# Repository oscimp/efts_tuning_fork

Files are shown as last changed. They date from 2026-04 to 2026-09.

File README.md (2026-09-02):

# <a href="https://efts.eu">European Frequency and Time Seminar (EFTS)</a> quartz tuning fork laboratory session.

A quartz tuning fork packaged in a transparent casing is used to demonstrate
* closed loop oscillation using a Negative Impedance Converter (NIC) circuit (<a href="oscillator/oscillateur_1night.png">Allan deviation</a> below $10^{-9}$ up to 30 s integration time).
* openloop stroboscopic imaging of the quartz prong motion driven by sound card output.

<a href=kicad/>KiCAD</a> board design files.



## References:

### Hardware (using a <a href="stroboscopy/IMG_20260409_120540_544.jpg">Raspberry Pi5</a> single board computer for running GNU Radio for controlling the sound card and recording the video stream):
* 32768 Hz tuning fork in transparent package: <a href="https://eu.mouser.com/ProductDetail/Epson-Timing/FC-135-32.7680KA-AC5?qs=f9yNj16SXrLM6nHs1T34rQ%3D%3D">Epson FC-135 32.7680KA-AC5</a> (0.404 euros/p)
* sound card with sampling rate 96 kHz or higher, e.g. <a href="https://www.amazon.fr/-/en/UGREEN-External-Headphones-Compatible-Raspberry/dp/B08Y8CZB2S/">UGREEN (10.2 euros on amazon)</a> although a <a href="http://www.thomann.fr/focusrite_scarlett_solo_3rd_gen.htm">Focusrite Scarlett Solo</a>
(89 euros but 192 kS/s at 24 bits) might be a wiser choice if can be afforded (see <a href="stroboscopy/">bottom of this page</a>).
* "digital microscope" webcam, e.g. <a href="https://amscope.co.uk/products/c-hhd510-w">AmScope HHD Series</a> (~50 euros)
* 7414 Schmitt trigger (0.5 to 0.7 euros)
* 7400 NAND gate (0.2 to 0.3 euros)

**Note**: the single board computer **must** be a RPi5 and **not** a RPi4 whose USB bus is too unstable to generate a clean audio signal probing
the narrow tuning fork resonance. See the <a href="stroboscopy">stroboscopy</a> subdirectory for the demonstration.

### Software

* use ``mplayer tv://`` to display the webcam output (or ``vlc`` if it displays properly in the
selected window manager): allows for stretching the image to full screen even if recording a "poor" 
webcam resolution (640x480) stream from the digital microscope.
* GNU Radio <a href="stroboscopy/snd.grc">flowchart</a> for driving the two channels of the
stereo sound card (tested with GNU Radio 3.10) with 1 Hz offset between the signal driving
the tuning fork and the stroboscopic signal driving the LED.
* Maybe wise to ``echo "performance" > /sys/devices/system/cpu/cpu0/cpufreq/scaling_governor`` 
to run the CPUs at maximum speed (will heat to 65 degC).

## Resources:

Equivalent BvD model of the quartz tuning fork (see <a href="KeysightE4990A/">the impedance analyzer</a> measurement):
* R1=53727 $\Omega$
* L1=7221 H
* C1=3.268 fF
* C0=3.368 pF

Quality factor $Q=\frac{1}{R1}\sqrt{\frac{L1}{C1}}=27700$

Resonance frequency $f=\frac{1}{2\pi\sqrt{L1\cdot C1}}=\frac{1}{2\pi\sqrt{7221\times 3.268\cdot 10^{-15}}}=32763$ Hz

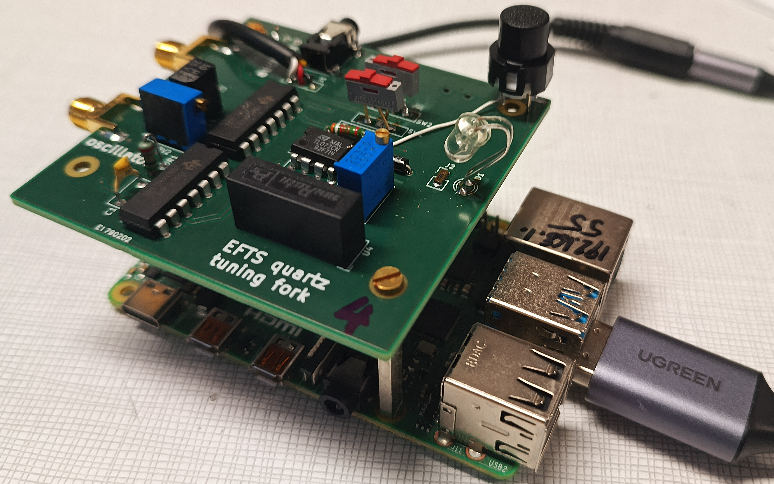
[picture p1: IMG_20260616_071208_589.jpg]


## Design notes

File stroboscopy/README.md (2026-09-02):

# Experimental setup: adjusting the LED position to illuminate the tuning fork

## Preliminary tests 

Notice that this picture is misleading as it shows a Raspberry Pi 4 which should
be avoided (see the bottom of this page) and replaced with a Raspberry Pi 5.

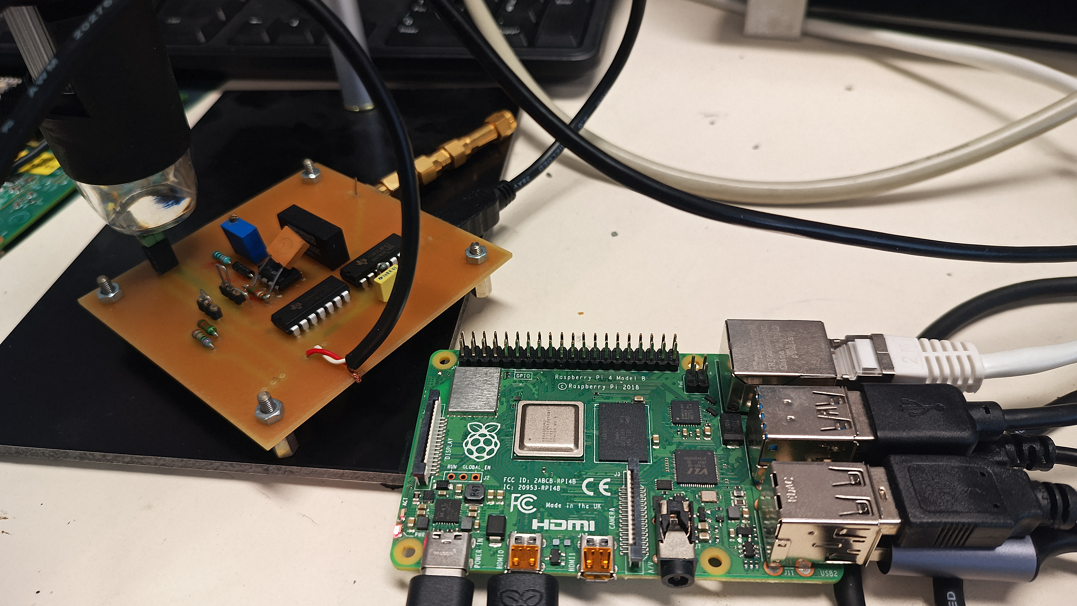
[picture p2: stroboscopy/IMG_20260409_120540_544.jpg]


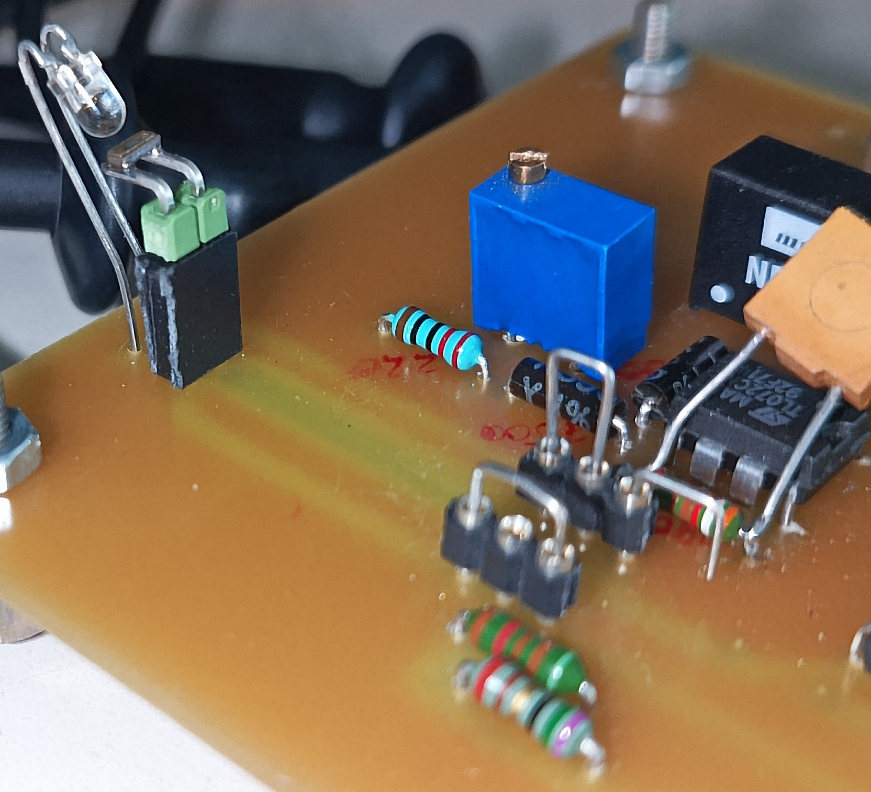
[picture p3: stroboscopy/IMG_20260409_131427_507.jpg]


## Oscilloscope screenshots: pulse driving the LED

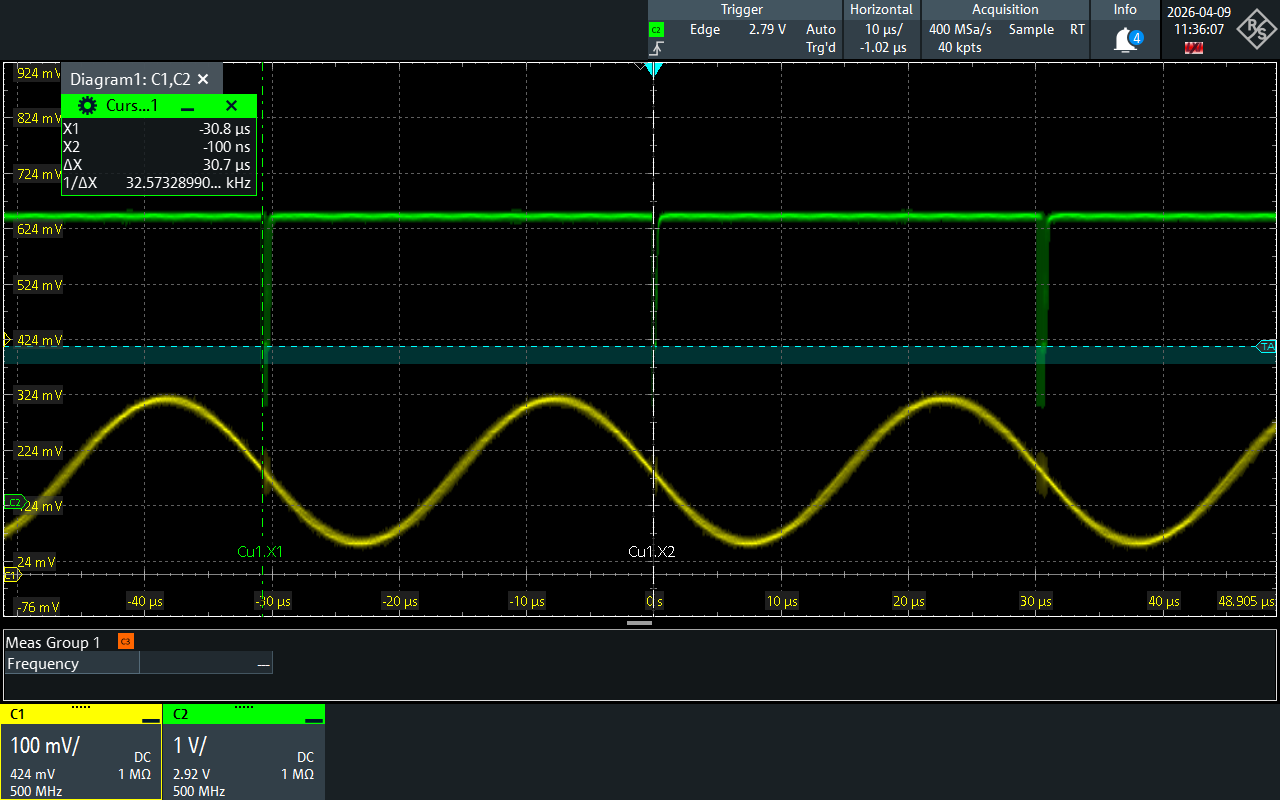
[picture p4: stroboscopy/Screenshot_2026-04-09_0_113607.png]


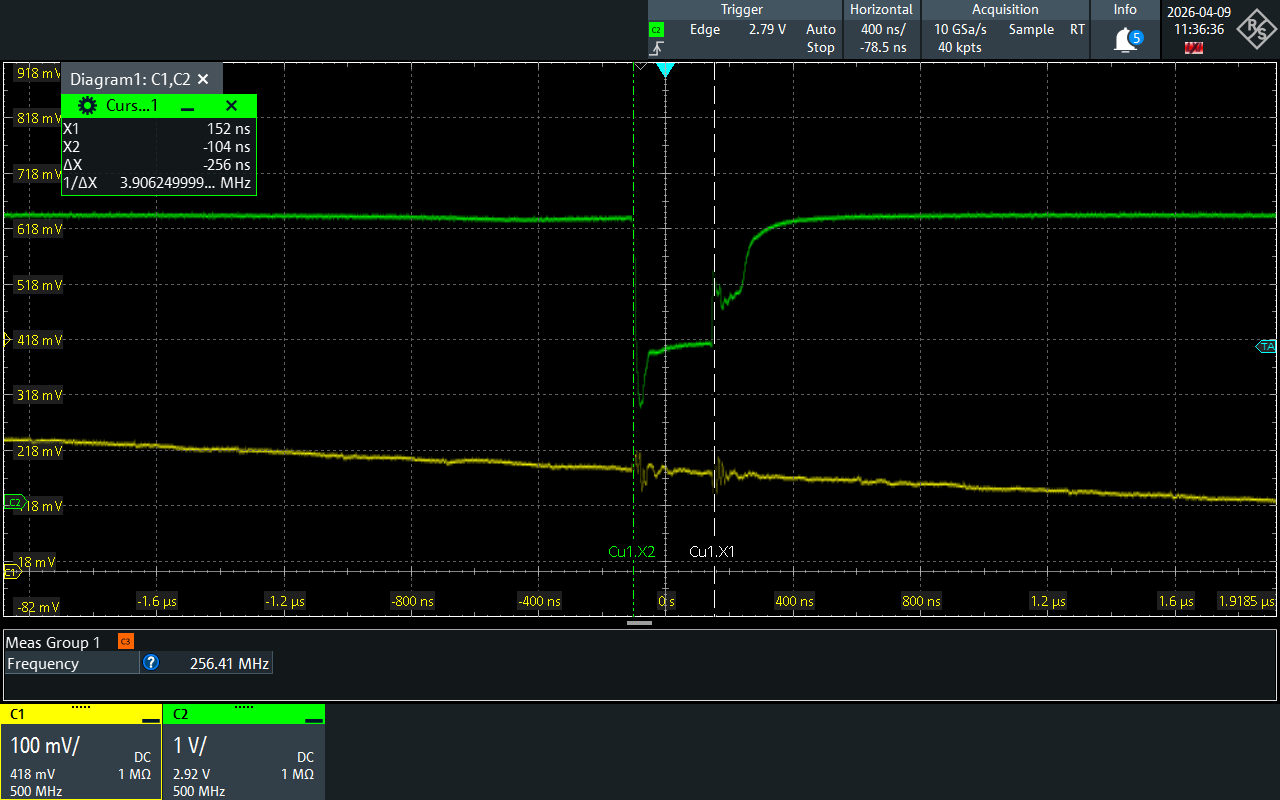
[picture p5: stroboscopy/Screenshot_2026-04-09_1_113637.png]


## Final setup

* On the Raspberry Pi: start the graphical user interface (``startx``),
open a terminal and launch ``alsamixer`` to check the sound card setting. Using F6,
select the USB sound card and check that the volume is maximum.

* Quit ``alsamixer`` and launch ``gnuradio-companion`` with the ``snd.grc`` flowgraph.
Select a frequency around 32764 Hz (a few Hz below 32768).

* Connect SPDT SW1 pin 1 to 2 (openloop measurement by driving the
tuning fork with the sound card) and SPDT SW2 1 to 3 (75 ohm load)

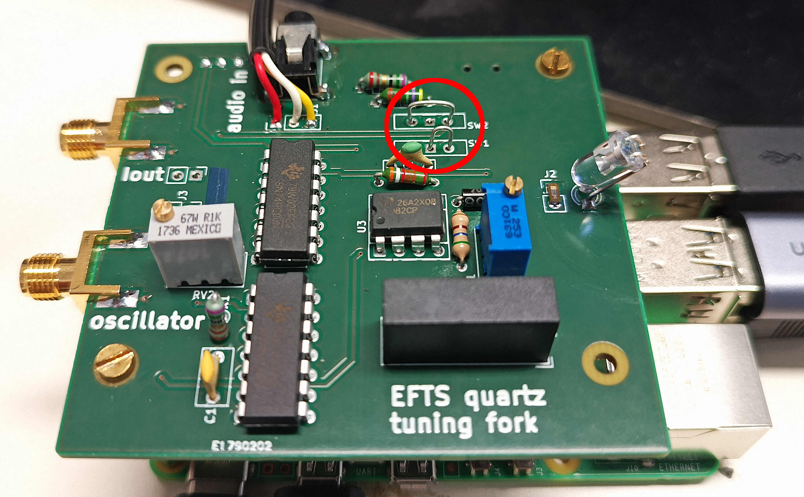
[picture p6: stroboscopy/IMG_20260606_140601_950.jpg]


* Adjust the voltage on pin 1 of the 7414 U2A using RV2

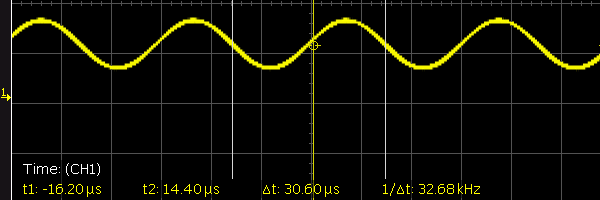
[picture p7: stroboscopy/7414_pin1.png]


so that its output in pin 2 toggles with
a more or less 50% duty cycle:

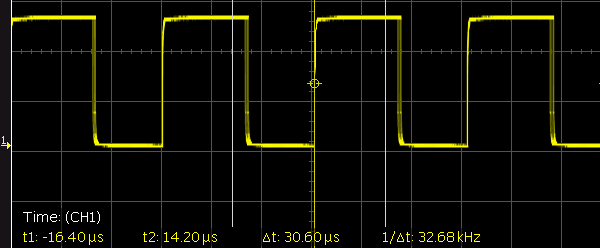
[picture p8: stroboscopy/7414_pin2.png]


* the voltage driving the LED must be a sharp negative pulse allowing the LED
to illuminate briefly the tuning fork:

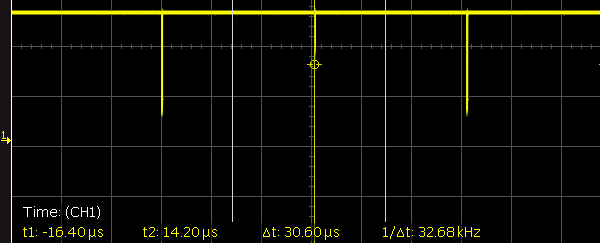
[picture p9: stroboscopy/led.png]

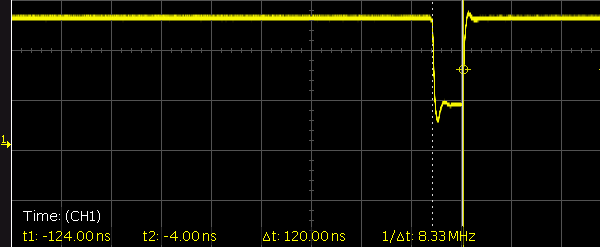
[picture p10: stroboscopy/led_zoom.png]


* check that the signal driving the tuning fork reaches the pin closest to the DC-DC
switching supply:

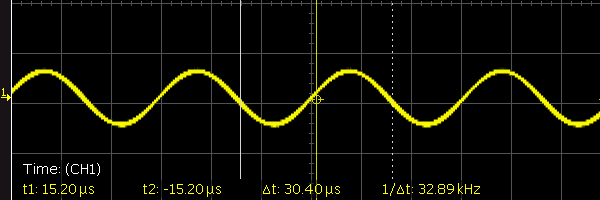
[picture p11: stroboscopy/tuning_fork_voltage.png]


* adjust the microscope position for the tuning fork picture to be centered and sharp

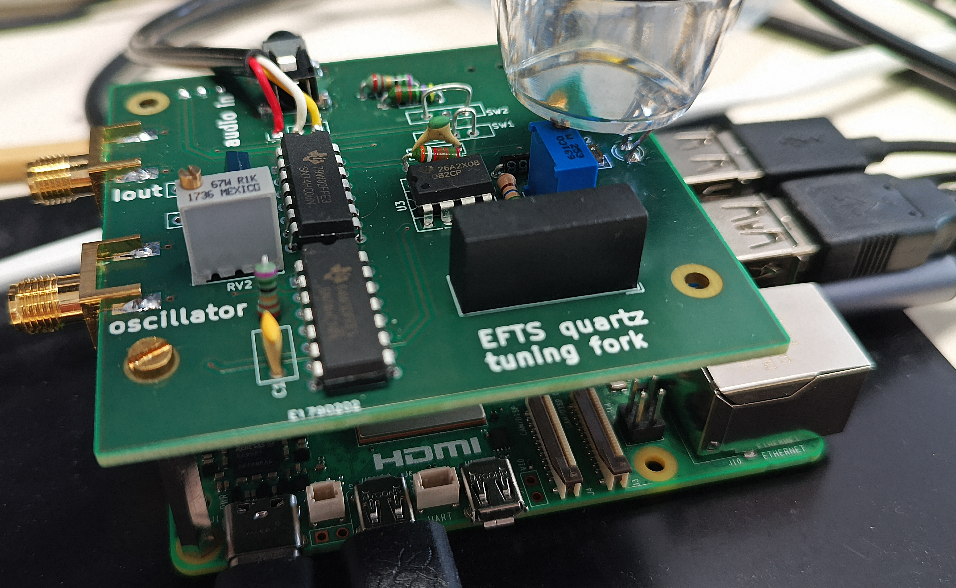
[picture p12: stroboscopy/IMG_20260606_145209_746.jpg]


<a href="https://superuser.com/questions/556029/how-do-i-convert-a-video-to-gif-using-ffmpeg-with-reasonable-quality">Converting AVI to animated GIF</a>:

```
ffmpeg -i vlc-record-2026-05-13-09h10m45s-v4l2____dev_video0-.avi -vf "fps=10,scale=320:-1:flags=lanczos,split[s0][s1];[s0]palettegen[p];[s1][p]paletteuse" -loop 0 vlc-record-2026-05-13-09h10m45s-v4l2____dev_video0-.gif
```

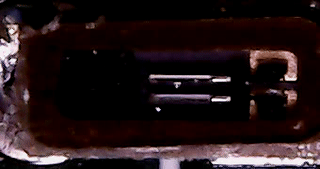
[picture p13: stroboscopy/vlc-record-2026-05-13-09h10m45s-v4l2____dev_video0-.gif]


## Automated mechanical displacement amplitude measurement

The script ``analyze.py`` replaces ``mplayer`` or ``vlc`` for collecting and displaying
images, but additionnally analyzes the displacement by correlating a reference measurement
in the first frame with all subsequent frames at the same location, marked with a green
line on each frame. The position and orientation of the green line is hardcoded, so the
tuning fork should be moved until one of the prongs is intersected by the green line. The
position is displayed in the terminal along the amplitude identified as the standard deviation
of a ring buffer collecting the position measurements. The pixel position is also saved in
``/tmp/pixel`` for plotting (e.g. GNU Octave as shown below) allows for recovering the sine-shaped
motion of the prong

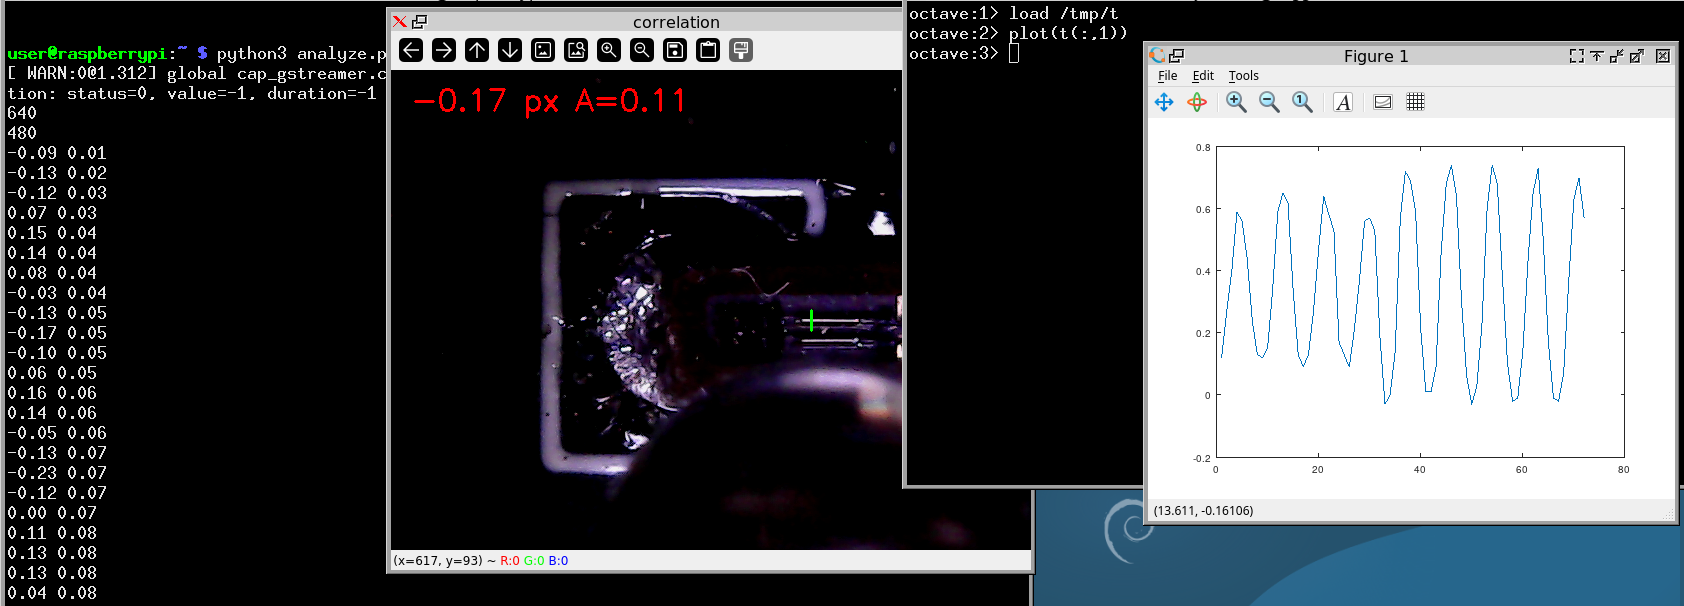
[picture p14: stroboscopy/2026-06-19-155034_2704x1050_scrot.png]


or using the GNUPlot script ``displ.plt`` which refreshes every second with the last 40
samples (vibration amplitude analysis window).

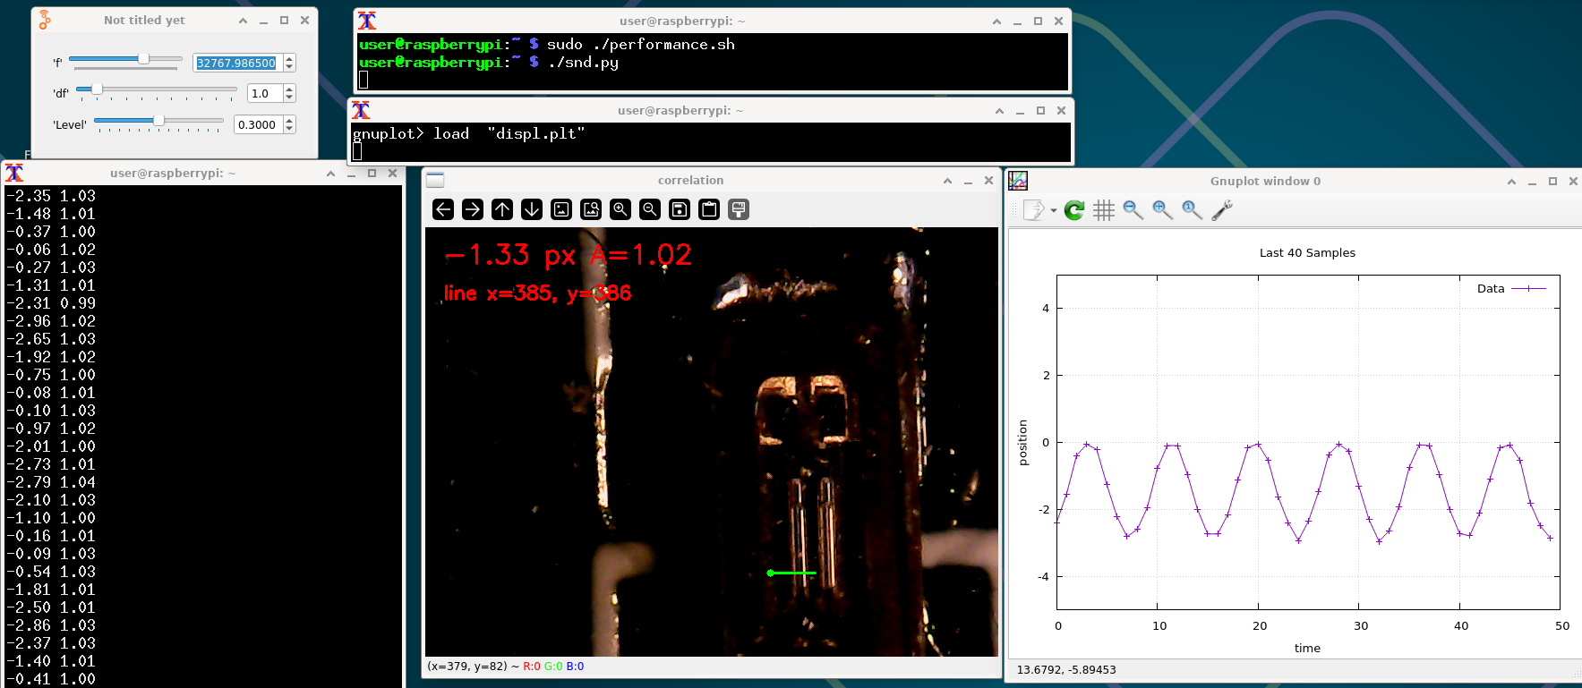
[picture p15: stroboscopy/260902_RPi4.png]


Executing ``analyze.py`` assumes that the package ``python3-opencv`` is installed.

## Problem with the RPi4 USB interface

Running a constant tone at the tuning fork resonance frequency on a Raspberry Pi 4 and
monitoring the current through the 50 kohm resistor between the tuning fork and ground exhibits
some unexpected jumps attributed to unstable signal generation by the sound card:

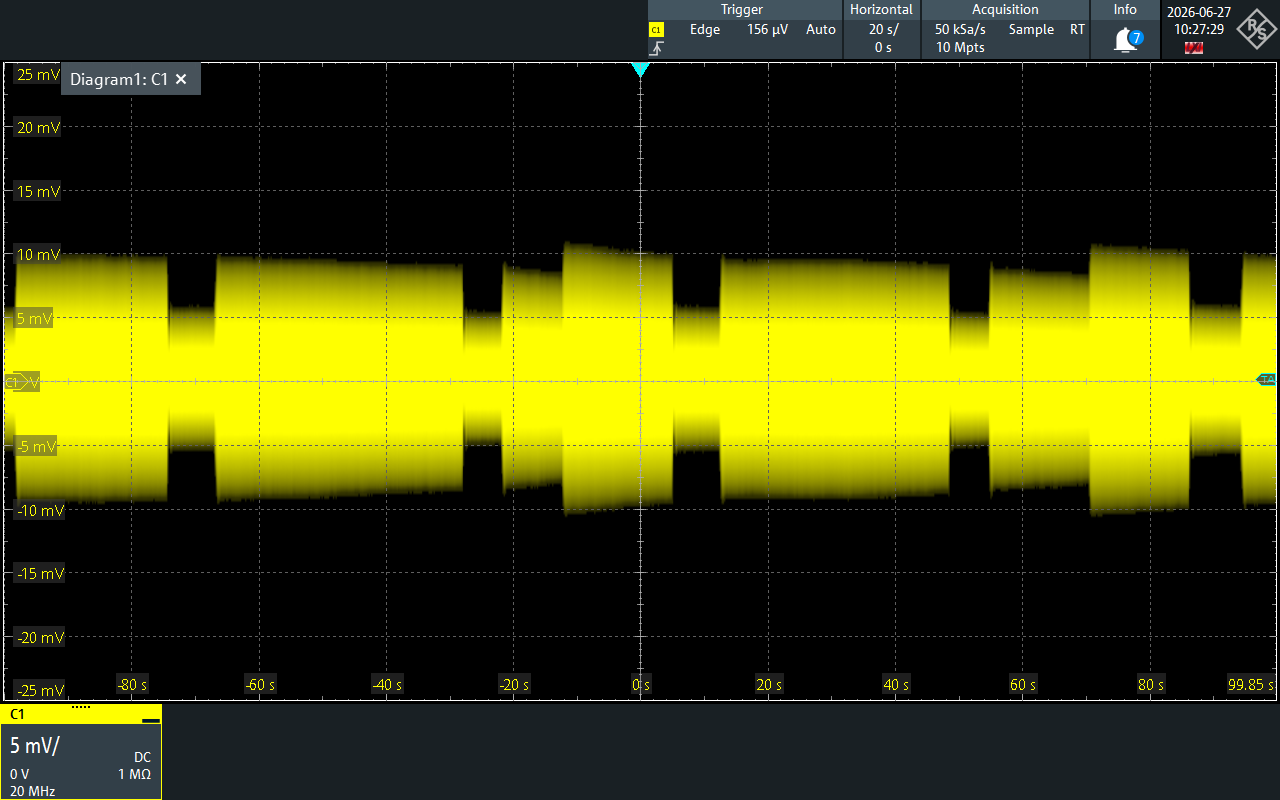
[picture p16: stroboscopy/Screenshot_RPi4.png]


most probably attributed to the poor latency performance of the RPi4 USB.

Same experiment on the Raspberry Pi 5, except at the end (80 s abscissa) when the frequency
was shifted by -2 Hz and back +2Hz on purpose to check that indeed the sound card was probing the 
tuning fork.

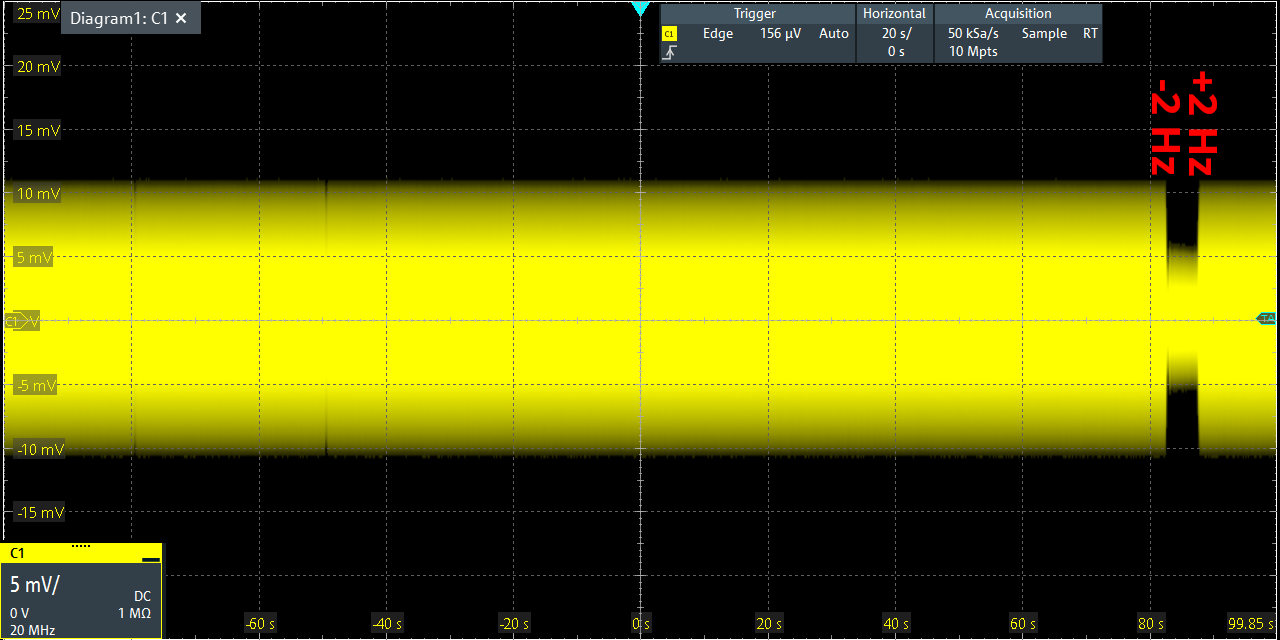
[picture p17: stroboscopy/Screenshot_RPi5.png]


Update Sept. 2026: long term measurements on the RPi5 also show some glitches on the sound card output

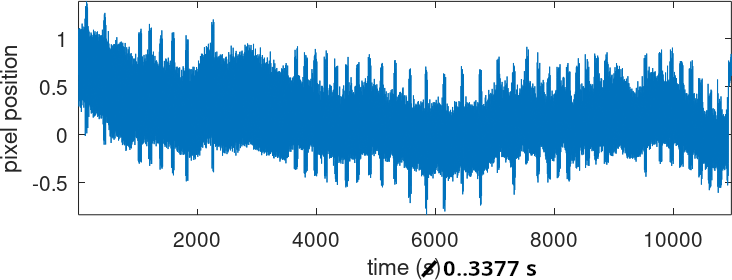
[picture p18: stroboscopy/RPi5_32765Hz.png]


although less pronounced than on the RPi4 under the same conditions.

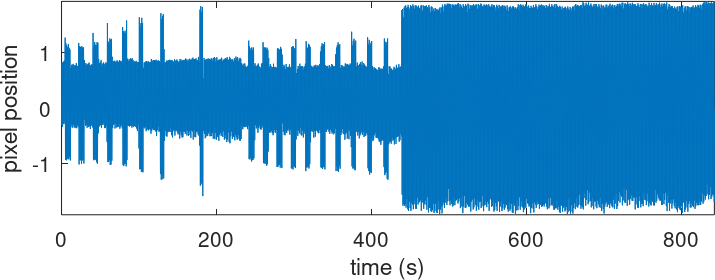
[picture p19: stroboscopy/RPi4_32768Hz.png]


A Scarlett Focusrite 18i8 provides much improved stability (and additional bandwidth and 24-bit quantization, at 10x the cost):

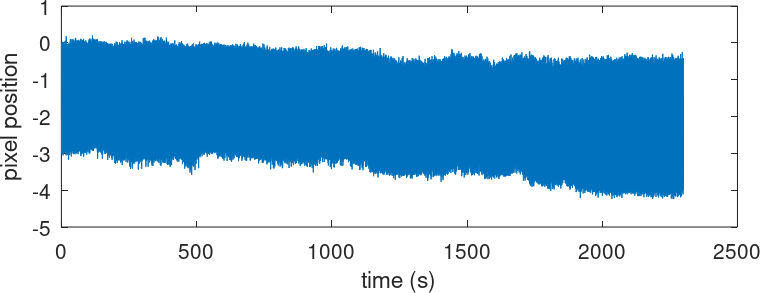
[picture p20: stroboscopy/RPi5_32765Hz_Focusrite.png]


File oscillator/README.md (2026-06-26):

See http://jmfriedt.free.fr/08520429.pdf for the description of the negative impedance circuit (Fig.3, page 7 of the PDF)
even though here any operational amplifier (e.g. TL72, TL82) will allow the 32768 Hz oscillator to start.

# Closed loop oscillator circuit

The startup time can be as long as a few minutes (hundreds of seconds).

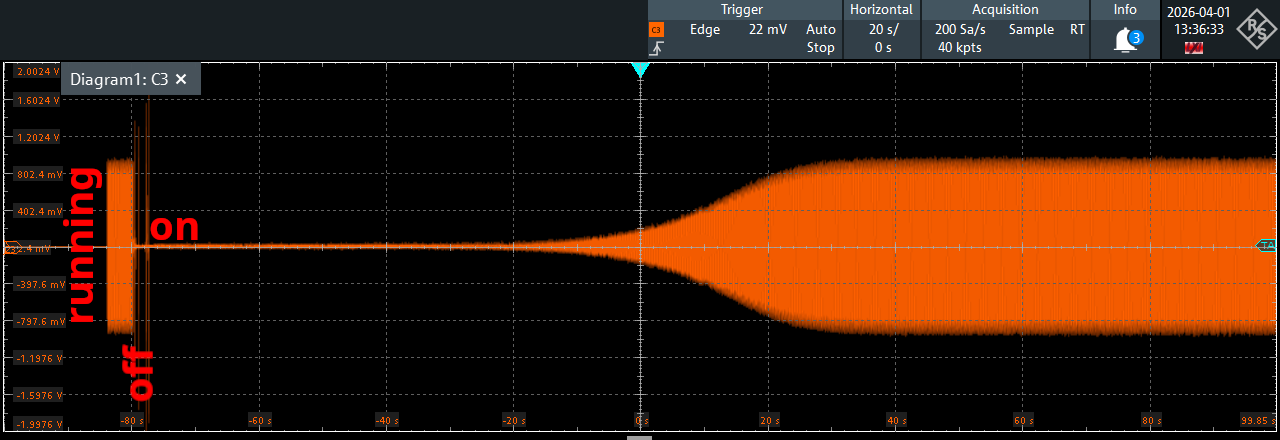
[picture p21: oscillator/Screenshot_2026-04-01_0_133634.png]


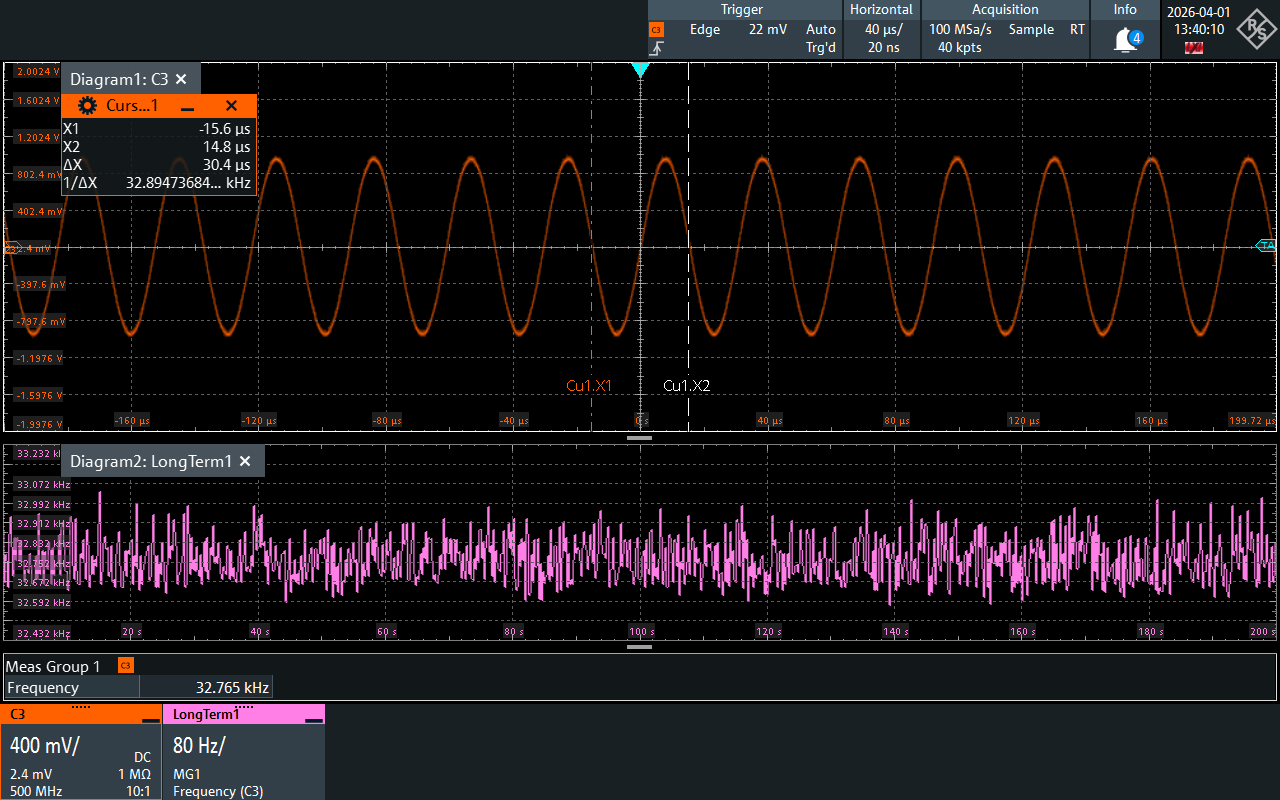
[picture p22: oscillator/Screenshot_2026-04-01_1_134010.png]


The modified Allan deviation of the frequency recording over one night
exhibits a sub- $10^{-9}$ relative frequency instability up to 30 second
integration time.

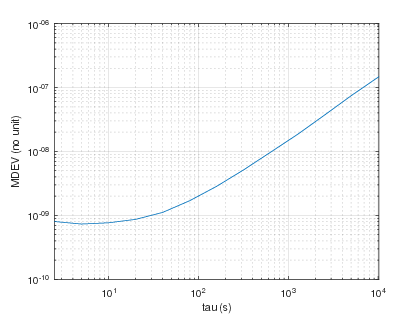
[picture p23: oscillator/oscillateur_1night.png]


## Setup

C4 was fitted with a 1 nF capacitor. In case the oscillator fails to start even at
the highest potentiometer value, remove C4.

* Close SW1 pin 2 and 3 to connect the tuning fork to the negative impedance converter circuit.

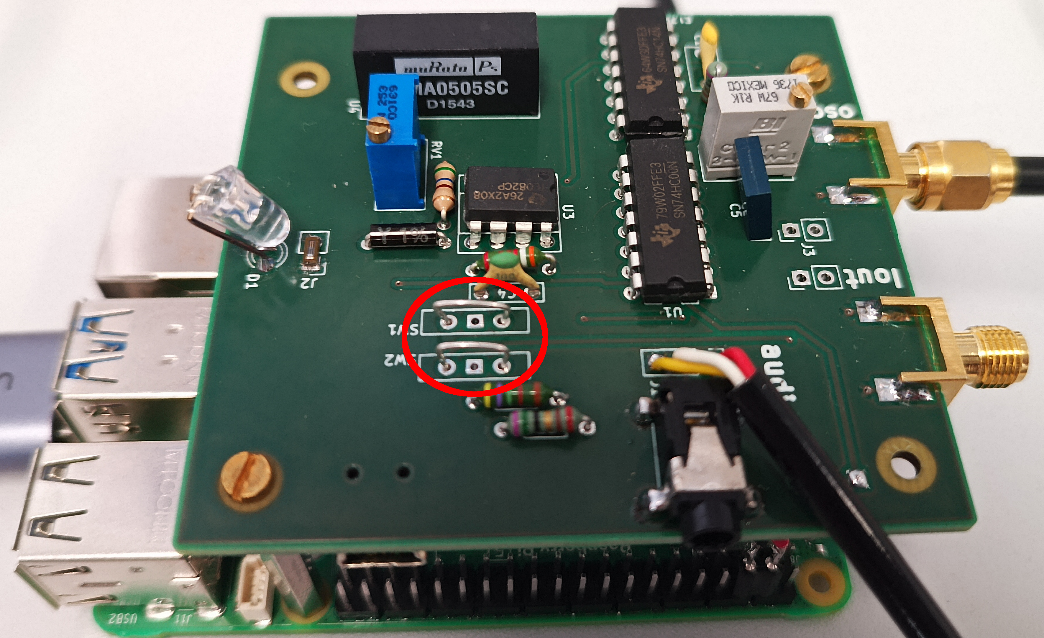
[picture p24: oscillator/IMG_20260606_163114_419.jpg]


* Adjust RV1 until the voltage on the Oscillator output SMA jumps from -4V to 0V by decreasing
the potentiometer resistance (turning counter-clock wise).

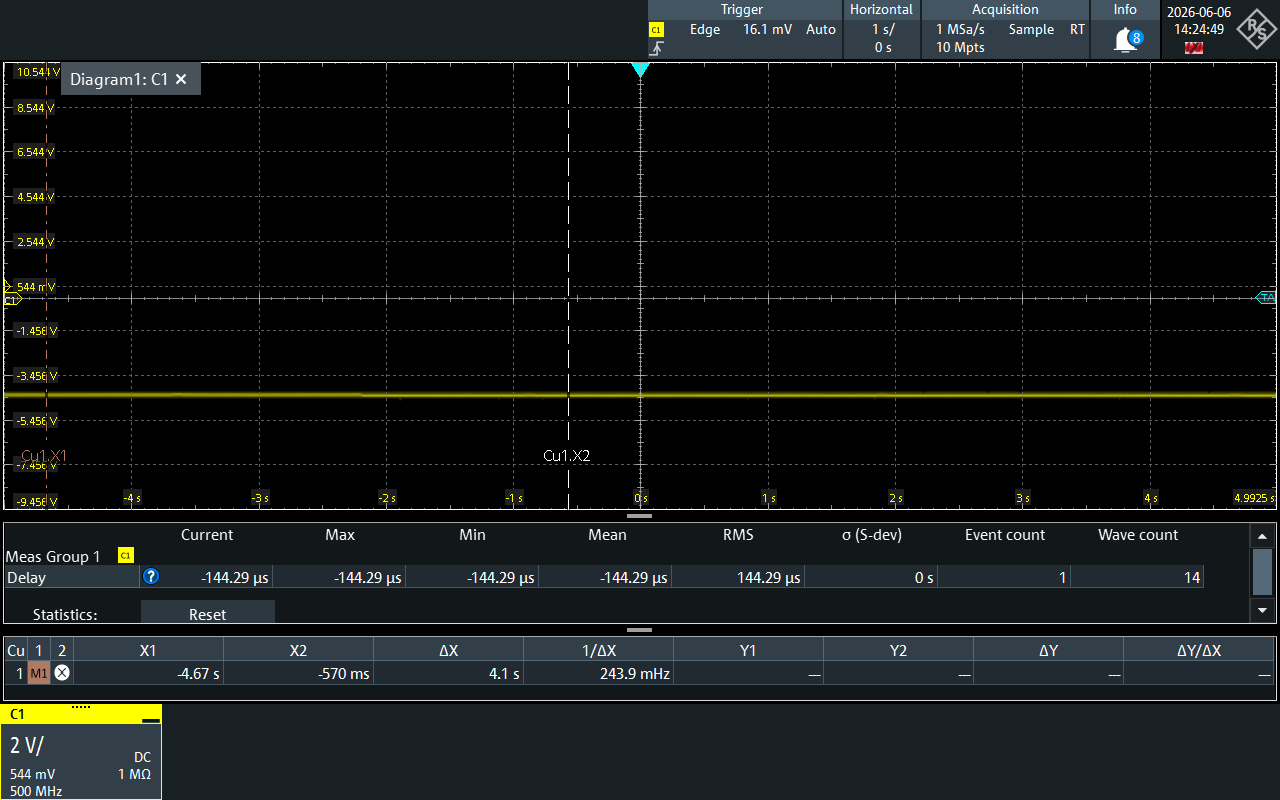
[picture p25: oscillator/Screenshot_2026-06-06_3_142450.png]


* Once the voltage is settled on 0V, increase the resistance (turn clock-wise) until the
oscillator starts.





In the following test (operational amplifier output connected to 50 ohms oscilloscope
channel) the oscillator returned to the -4V fixed value:



## Oscillator startup time

The oscillator starts by amplifying thermal noise until the non-linear (saturation) behaviour of the amplifier compensating
the resonator losses is reached, preventing further amplitude growth.
1. the thermal noise in the resonator bandwidth is $\sqrt{R_1.k_B.T.B}$ with $R1=53727$ ohms and $B$ the resonator bandwidth $f0/Q\simeq 1$ Hz
so that the initial thermal voltage noise is 15 nV
2. the final amplitude is 1 V (see screenshots) reached by an exponential growth $\exp(t/\tau)$ with $\tau=Q/(\pi f0)\simeq 0.3$ s: $-ln(15e-9)=18$ so the startup time constant is about 6 seconds
3. the resonator $R_1$ is compensated for by the NIC negative impedance $-R_N$ and oscillation occurs if $|R_N|<R_1$. Stating $G_N=1/R_N$ and $G_1=1/R_1$, the excess gain is $G_N-G_1$ and the startup time is scaled by $G_1/(G_N-G_1)$ which can become significant if $G_N-G_1\rightarrow 0$

### Demonstration

* A voltage $V$ develops accross the resonator so that the losses are $P_{loss}=V^2.G_1$ with $G_1=1/R_1$ at resonance where the BvD model only includes the motional resistance
* the NIC behaves as $-R_N$ so the power injected by the NIC is $P_{NIC}=V^2.G_N$
* the budget is $P_{NIC}-P_{loss}=V^2(G_N-G_1)$ and the power is the energy variation so $dE/dt=V^2(G_N-G_1)$ and since $E\propto V^2$ then $dV/dt=(G_N-G_1)V$ with a solution $V(t)=\exp(At)$ with $A\propto G_N-G_1$ as was the case for $1/\tau$ before.

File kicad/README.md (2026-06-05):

# KiCAD schematic and board design files.

The non-plated through holes have been placed with a spacing compatible with
installing the board on top of a Raspberry Pi 4/5 single board computer for
a compact setup. Whether the heat dissipated by the processor will affect
the resonator performance remains to be demonstrated.



The potentiometer closest to the audio input aims at adding a DC offset to bring
the audio output within the range of the Schmitt trigger toggling voltage. Set
the sound card output to maximum amplitude to increase chances of the Schmitt 
trigger toggling. The potentiometer further from the audio input is the negative
impedance and should be tuned so that the oscillator starts (slowly !) at resonance
frequency of the tuning fork.

The setup is designed to be assembled on a Rapsberry Pi 4/5:





## Schematic



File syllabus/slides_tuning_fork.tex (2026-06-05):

\documentclass[compress,10pt,aspectratio=169]{beamer}
%\setbeamertemplate{background canvas}[bottom=white,top=structure.fg!25]
%\usetheme{Hannover}
\setbeamertemplate{headline}{}
\setbeamertemplate{footline}{June 27, 2020 - SDRA}
\setbeamersize{text margin left=0.6cm}
\usepackage{appendixnumberbeamer}
\usepackage{hyperref,listings,picinpar,mathtools} % ,enumitem}
\usepackage{color}
\settowidth{\leftmargini}{\usebeamertemplate{itemize item}}
\addtolength{\leftmargini}{\labelsep}

\beamertemplatenavigationsymbolsempty

\usepackage{listings,hyperref,multicol}
\usepackage{color,cancel}

\usepackage{listings}
\usepackage{color}

\definecolor{grey}{rgb}{0.95,0.95,0.95}
\definecolor{red}{rgb}{1.0,0.0,0.0}
\definecolor{green}{rgb}{0.0,0.7,0.0}
\definecolor{blue}{rgb}{0.0,0.0,1.0}
\lstloadlanguages{bash,Java,C,C++,csh,make,sh}%%[Visual]Basic,xml}
\lstset{frame=none,basicstyle=\footnotesize,breaklines,tabsize=2,captionpos=b,prebreak={\hbox{$\rightarrow$}},postbreak={\hbox{$\hookrightarrow$}},showstringspaces=false,backgroundcolor=\color{grey}\bfseries,keywordstyle=\color{blue},commentstyle=\color{green}\textit,stringstyle=\color{red}\ttfamily,abovecaptionskip=2pt,aboveskip=0pt,belowskip=0pt,belowcaptionskip=0pt}
%\lstset{moredelim=[is][\color{red}]{_+_}{_+_}}

\graphicspath{{/home/jmfriedt/enseignement/diapason/}{/home/jmfriedt/femto/sipat/hdr/}{/home/jmfriedt/femto/sipat/}{/home/jmfriedt/femto/sipat/hdr/imec/summary_imec/}{/home/jmfriedt/femto/sipat/hdr/eftf09/}{/home/jmfriedt/femto/sipat/hdr/Presentation/Imagez/}{/home/jmfriedt/femto/sipat/hdr/fit_parabole/}{/home/jmfriedt/femto/sipat/hdr/gps_scan/}{./hdr/allan_gps/}{/home/jmfriedt/senseor/projets/lovefood/140226_freiburg/}{/home/jmfriedt/senseor/projets/lovefood/simulations/lovefood/130115_lovefood/}} % DOIT avoir / a la fin

\beamertemplatefootpagenumber

\usepackage{graphicx,verbatim,multicol}
%\usepackage[pdftex,colorlinks=true,bookmarks=true,bookmarksopen=true,pagebackref=false,breaklinks=true,pdfauthor={Jean-Michel FRIEDT}]{hyperref}

\begin{document}

\title{Quartz tuning fork stroboscopic displacement field measurement}
\author[J.-M Friedt]{J.-M Friedt\\ \ \\ 
FEMTO-ST/Time \& Frequency department \\ \ \\ jmfriedt@femto-st.fr \ \\ \ \\
slides and references at \url{jmfriedt.free.fr}}
\maketitle

\section{Introduction}
\begin{frame}[fragile]\frametitle{Quartz tuning fork}

\vspace{0.1cm}
\hspace*{7.68cm}
\vspace{-5.1cm}

\noindent
\begin{itemize}
\item the ``quartz'' in quartz watch
\item the time reference is given by a tuning fork
\footnote{W.E. Newell, {\em Miniaturization of tuning forks}, Science {\bf 161} (3848), 1320--1326 (1968)}
\footnote{later an atomic transition from an atom in the Cs clock} \\
vibrating at $32768=2^{15}$~Hz $\Rightarrow$ 
counter (binary\\ frequency divider) to reach 1~Hz
\item piezoelectricity as an efficient way of \\generating mechanical vibration under control\\
of an electrical signal
\item acoustic signal: compact component since \\wave velocity is shrunk by
$10^5$ with respect to\\ electromagnetic (10~km $\rightarrow$10~cm)
\item initially a single beam vibrating at a few kHz: many spurious modes + lower quality factor
\item 1960: replace a single beam with a tuning fork (Seiko Quartz Astron at 8192~Hz)
\item from an engineering perspective: tuning fork = electrical dipole with extremely high
quality factor
\item from a physicist perspective: vibrating prongs made of a piezoelectric crystal
\end{itemize}

\vspace{0.05cm}
\end{frame}

\begin{frame}[fragile]

\vspace{-.21cm}
\begin{minipage}[t]{\linewidth}
\begin{minipage}{.49\linewidth}
\begin{itemize}
\item Tuning fork fundamental mode frequency
\vspace{-0.4cm}
$$f_0\simeq 0.1615\frac{w}{L^2}\sqrt\frac{E}{\rho}$$ 
\vspace{-0.4cm}

{\footnotesize with length $L\simeq
3.36$~mm and width $w\simeq 436$~$\mu$m, Young modulus
$E\in 75:100$~GPa (anisotropic) and density $\rho\simeq 2650$~kg/m$^3$ -- 
N.A: $f_0\in [33:38]$~kHz\par}
{\tiny L. Bates {\em \& al.}, {\em Determination of the temperature dependence
of Young's modulus for stainless steel using a tuning fork}, J. Undergrad.
Res. in Physics {\bf 18} (1), 9--13 (1999)\par}
{\tiny {\bf Note:} J. Falter {\em \& al.}. {\em Calibration of quartz tuning fork spring constants ...} 
(2014): the length of the prong should be to the stress minimum $>$ geometrical length\par}
\item high $Q\simeq 70000$ (drops to 7000 in air)
\item $Q$ is defined as the stored energy/energy dissipated
during each oscillation
\item the time needed to release the stored energy is $Q/\pi$
oscillations or $Q/(\pi f)$~s @ $f=32768$~Hz
\item in an second order resonator circuit, the width at half
height of the resonance (real part of admittance) is $\delta f=f/Q$
\item low temperature coefficient
\end{itemize}
\end{minipage}
\begin{minipage}{.53\linewidth}

\end{minipage}
\end{minipage}
\end{frame}

\begin{frame}[fragile]\frametitle{Quartz tuning fork characterization}

We wish to characterize the tuning fork electrical transfer function $Y(f)$ by sweeping $f$ and monitoring
the current (measured as voltage on a load resistor)

\hfill

Questions:
\begin{enumerate}
\item what is the frequency step $df$ at which $f$ must be swept~?
\item how long shall we wait between two steps of $df$
\end{enumerate}
\vfill
$\Rightarrow$ challenge: observe the tuning fork prong motion using a personnal computer sound
card and a commercial, off the shelf (COTS) webcam
\end{frame}

\begin{frame}[fragile]\frametitle{Sound card}

\begin{itemize}
\item Many current sound cards will exhibit $>$48~kS/s sampling rate (usually 96~kS/s or 192~kS/s)
\item Driving the 32768~Hz tuning fork with this signal is possible ...
\item ... but COTS webcams exhibit much lower framerate -- 25 or 30~fps
\item Can we ``freeze'' the prong \\motion during such long \\
(40-33~ms) exposures~?
\item Yes if the tuning fork is only \\illuminated when the prongs \\
are in the same position: \\{\bf stroboscopy}
\end{itemize}
\vspace{-2.8cm}
\hfill
\end{frame}

\begin{frame}[fragile]\frametitle{Stroboscopic setup}
However, illuminating for a short duration (1/10th of the period is 3~$\mu$s or 300~kHz bandwidth)
is way beyond the capability of a sound card \\
$\Rightarrow$ dedicated hardware controlled by
a stereo sound card.

\begin{itemize}
\item Pulse = convert a sine wave to a square wave and to a pulse
\item Pulse = phase shifted copies of the same sine wave
\item Phase shift = time delay = RC circuit
\item sine $\rightarrow$ Schmitt trigger (square, 2) $\rightarrow$ RC delay $\rightarrow$ Schmitt trigger (square) $\rightarrow$ \& with (2) $\rightarrow$ pulse
\end{itemize}

\only<1>{
}
\only<2>{
}
\end{frame}

\begin{frame}[fragile]\frametitle{Hardware setup: the bias T}

\begin{itemize}
\item a digital gate triggers around 1.5~V
\item sound card output is 0-mean value
\item offset the mean value without changing the AC spectral characteristics: bias T
\end{itemize}

\hfill

\vfill {\bf Question:} considering the resistors have been selected as 1~k$\Omega$ resistances so that the current
in the voltage divider bridge is $DC/2$~mA, how do we select the capacitor value so that the bias T output
is the sum of DC+AC around 32768~Hz~?
\end{frame}

\begin{frame}[fragile]\frametitle{Image processing}

Movies (.avi format) have been recorded for various $f$ driving frequencies

\begin{enumerate}
\item Decompose each movie to a series of pictures ({\tt mplayer -vo jpeg movie.avi})
\item Select an area representative of the prong motion
\item Compute the displacement of
this area as the \\
cross-correlation maximum position between
the \\first image and the second image

\only<1>{
\vspace*{-1.52cm}
\hspace*{7.5cm}
\vspace*{-1.62cm}
}

\item Repeat for all images, cross-correlating the \\$N$th image with the first
\item Display the motion of the prong
\only<2>{

\vspace*{-2.93cm}\hspace*{7.5cm}
\vspace*{-0.3cm}
}
\item Since the motion is only a few pixels, we use an \\oversampling technique of fitting the correlation 
\only<3>{\\}
maximum and identifying the position of the fit \only<3>{\\}maximum
\item Repeat for each frequency
\only<3>{

\vspace*{-4.7cm}
\hspace*{7.5cm}
}
\end{enumerate}
\end{frame}

\begin{frame}[fragile]\frametitle{Meaning of ``super-resolution''}

{\footnotesize
The correlation can detect sub-pixel displacement, as demonstrated here by oversampling the signal
for sub-sampling period displacement\par}

\vspace{0.081cm}
\begin{minipage}[t]{\linewidth}
\begin{minipage}{.50\linewidth}
\lstinputlisting[language=Python,basicstyle=\tiny]{demo_polyfit.py}
\end{minipage}
\begin{minipage}{.49\linewidth}
\vspace{-0.8cm}


\vspace{-0.2cm}
fractional value of the correlation max {\bf position}\\
991.99 ~~ (oversampling by FFT, zero padding \\
992.05 ~~ and iFFT)\\
992.11\\
992.18\\
992.29\\
...

\end{minipage}
\end{minipage}
\end{frame}

\begin{frame}[fragile]\frametitle{For more information ...}

\vspace{-0.1cm}
Tuning fork:
{\footnotesize
\begin{enumerate}
\item T. Hunkin \& R. Garrod, {\em Secret Life Of Machines:
The Quartz Watch} (1991), at \url{https://www.youtube.com/watch?v=nQ9_bOIj49s}
\item M.A. Lombardi, {\em The Evolution of Time Measurement, Part 2: Quartz Clocks},
IEEE Instrumentation \& Measurement Magazine (Oct. 2011), pp.41--
\item J.-M Friedt, \'E. Carry, {\em Introduction au diapason \`a quartz}, Bull. de l'Union des Physiciens {\bf 879} 1137--1146 (2005) [in French]
\item J.-M Friedt, \'E. Carry, {\em Introduction to the quartz tuning fork}, American Journal of 
Physics, pp.415-422 (2007)
\item J.Marc, C. Canard, A. Vailly, V. Pichery, J.-M. Friedt, {\em Le diapason \`a quartz comme 
capteur~: utilisation de la carte son de PC pour l'instrumentation}, Bull. de l'Union des Physiciens {\bf 958}, pp.1051--1073 (2013) [in French]
\item J.-M. Friedt, {\em Mesure stroboscopique du champ de d\'eplacement d'un diapason \`a quartz 
au moyen d'une carte son et d'une webcam}, Bull. de l'Union des Physiciens {\bf 999} (2017) [in French]
\end{enumerate}
}

Stroboscopy:
{\footnotesize
\begin{enumerate}
\item N.S. Gingrich, {\em Stroboscopic Aids in the Teaching of Physics}, American Journal of 
Physics {\bf 5}, 277 (1937)
\item S. Gupta \& B. Jalali, {\em Time stretch enhanced recording oscilloscope}
Appl. Phys. Lett. {\bf 94}, 041105 (2009)
\item J.S. Baskin \& A.H. Zewail, {\em Freezing Atoms in Motion: Principles of 
Femtochemistry and Demonstration by Laser Stroboscopy}, J. Chem. Educ. {\bf 
78} (6), p 737 (2001)
\end{enumerate}
}
\end{frame}

\begin{frame}[fragile]\frametitle{Software for image processing example}

GNU/Octave version\vfill

\begin{lstlisting}[language=Octave,basicstyle=\tiny]
pkg load signal
frequence=[32728:32753]; films=dir('./?????.avi');
for nfilm=1:length(films)
  system('rm -f ./*jpg');
  system(['mplayer -vo jpeg ./',films(nfilm).name]);
  d=dir('./*.jpg');
  x=imread(d(20).name);
%  figure(1);imagesc(x);
  x=x(:,:,1);
  reference=x(440,492:600);
  reference=reference-mean(reference);
  m=1;
  for k=21:180
    x=imread(d(k).name);
    x=x(:,:,1);
    mesure=x(440,492:600); 
    mesure=mesure-mean(mesure);
    xc=xcorr(reference,mesure);
    [a(m),b(nfilm,m)]=max(xc);
    [u,v]=polyfit([b(nfilm,m)-2:b(nfilm,m)+2],xc([b(nfilm,m)-2:b(nfilm,m)+2]),2);
    xi=linspace(b(nfilm,m)-2,b(nfilm,m)+2,1024);
    yi=polyval(u,xi);
    [aa,bb]=max(yi); solution(m,nfilm)=xi(bb);
    m=m+1;
  end
%  figure(2);plot(solution-mean(solution));hold on
  amplitude(nfilm)=std(solution(:,nfilm))
end
\end{lstlisting}
\vfill
%Movies at \url{http://jmfriedt.org/TP_diapason.tar.gz}
\end{frame}
\end{document}

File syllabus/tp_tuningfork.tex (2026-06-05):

\documentclass[a4paper]{article}

\usepackage{graphicx,url,fullpage,fourier}
\textwidth=18.5cm
\oddsidemargin=-1.2cm
\textheight=26cm
\topmargin=-1.52cm
\usepackage{listings,color,hyperref,picinpar}

\lstset{language=C}
\definecolor{gris}{rgb}{0.95,0.95,0.95}
\definecolor{mygreen}{rgb}{0,0.6,0}
\definecolor{mygray}{rgb}{0.5,0.5,0.5}
\definecolor{mymauve}{rgb}{0.58,0,0.82}

\lstset{ %
  backgroundcolor=\color{gris},
  basicstyle=\footnotesize,   
  breakatwhitespace=false,   
  breaklines=true,          
  captionpos=b,            
  commentstyle=\color{mygreen},
  deletekeywords={...},       
  escapeinside={\%*}{*)},          % if you want to add LaTeX within your code
  extendedchars=true,        
  frame=single,             
  keepspaces=true,         
  keywordstyle=\color{blue},
  language=Octave,       
  morekeywords={*,...}, 
  numbers=left,        
  numbersep=5pt,      
  numberstyle=\footnotesize\color{mygray}, 
  showspaces=false,   
  showstringspaces=false,
  showtabs=false,       
  stepnumber=2,         
  stringstyle=\color{mymauve},
  tabsize=2,                 
  title=\lstname                   % show the filename of files included with \lstinputlisting; also try caption instead of title
}

\begin{document}
\begin{center}
{\bf \Large Quartz tuning fork resonator stroboscopic displacement field mapping}\\ \ \\
J.-M Friedt, \today
\end{center}

Quartz resonators are core components in all systems requiring a clock signal -- most significantly
all synchronous digital systems (i.e. microprocessors/microcontrollers). While bulk acoustic resonators
are available for frequencies ranging from a few hundred kHz to a few hundred MHz (using overtones),
the most common quartz resonator geometry is the tuning fork. This geometry, used in all so called
quartz watches \cite{slom}, has evolved from the basic beam geometry to eliminate unwanted modes by using 
symmetry considerations to cancel symmetric modes. Odd overtones are well separated in frequency to be electrically filtered.
Hence, a mechanical vibration is the basic underlying principle of most stable watches, with the drawback 
of a sensitivity to environmental conditions changing the acoustic velocity of the quartz substrate -- most
significantly temperature -- yielding to some long term drift compensation strategy as found in atomic clocks.
The topic we wish to address in this laboratory session is mapping the displacement of the quartz tuning fork
resonator, along the beam length and depending on the frequency.

\noindent
\fbox{\parbox{\linewidth}{This laboratory experiment only requires a computer fitted with a sound card sampling at 192~kHz, a USB bus,
a webcam, and less than 10~euro worth of electronic components. It is designed to be easy to reproduce.}}

\section{Introduction}

While a resonator is classically used in a closed loop configuration as an oscillator, characterizing
the spectral characteristics of the tuning for is most easily achieved by using an open-loop approach
\cite{jm0,jm1}. Commercial
instruments -- network analyzers -- perform this task extremely well, but are expensive and do not provide the
signals needed to visually observe the displacement of the prongs. Hence, our first objective is to assemble a 
stable signal source: the source must exhibit a better frequency stability than the object under investigation.
Considering the excellent frequency stability of quartz resonators and their high quality factor, only a quartz
controlled synthesizer (as opposed to a LC low-frequency generator) provides the targeted stability. One such generator is a sound
card \cite{jm2}. Furthermore, stereo sound cards are ideally suited to the targeted purpose: one channel will be used to power
the tuning fork and the second channel will drive the voltage of a LED used to illuminate the tuning fork prongs in order
to achieve a stroboscopic lighting. Hence, any low-cost webcam with an exposure duration longer than the oscillation
period will allow visualizing the prong motion, at an equivalent frequency equal to the difference of the frequencies
between the signals driving the tuning fork and driving the light source \cite{jm3}.

The MEMS characterization tool we will develop during this laboratory session is a simplified
version of such fancy instruments as Poytec's MSA-500 Micro System Analyzer as shown at
\url{http://photonic-technologies.info/eu/products/vibration-sensors/microscope-based-systems/msa-500-micro-system-analyzer/}.

\begin{figwindow}[1,r,, %audio_grc.png},
{GNU Radio flowchart for programming the two stereo outputs with a given user-defined frequency, one of the
channels being offset by 1-Hz with respect to the other.}\label{grc}]
The opensource GNURadio framework allows for defining both stereo channel frequencies, sweeping the frequency source,
and keeping a constant offset between both channel frequencies (Fig. \ref{grc}). However, the stroboscopic illumination pulse must
be short with respect to the period. While a 192~kHz sampling rate meets Nyquist criterion when generating a $32768=2^{15}$~Hz
signal -- the nominal resonance frequency of most tuning forks -- it will not be sufficient to generate a pulse lasting
about 1/10th of the period. Hence, a dedicated pulse generation circuit must be assembled to drive the LED.
\end{figwindow}

{\bf
\begin{enumerate}
\item A tuning fork resonance frequency is 32768~Hz. Find a quartz tuning\\
fork datasheet: what is the typical quality factor of a packaged tuning \\
fork? what is the frequency resolution needed to observe the\\ resonance 
in a network analyzer configuration?
\item When the tuning fork package is opened and the vibrating element \\
exposed to air, the quality factor drops 10-fold due to viscous drag. \\What 
is the frequency resolution needed to observe the resonance \\
frequency once  the sealed packaging has
been opened?
\item What is a stroboscopic illumination strategy to observe objects moving quickly but periodically?
\end{enumerate}
}

\section{Stroboscopic signal generation}

A stroboscopic signal meets two requirements:
\begin{itemize}
\item the period is close to the driving signal: the frequency difference between the device-under-test
driving signal and the stroboscopic signal defines the speed at which the phenomenon under investigation is observed.
\item the duration of the illumination is ``much'' shorter than the period to give the feeling that each 
frame is frozen in time. Too long an illumination with respect to the phenomenon period will blur the image.
\end{itemize}

\begin{figwindow}[0,r,,{Assembled stroboscopic signal
generation circuit}\label{2}]
Generating the pulse driving the LED must be addressed at the hardware level (Fig. \ref{2}). 
One classical method for generating short pulses
is to use two Schmitt triggers: the sine wave generated by the sound card is converted to a square
wave using the first stage of a Schmitt trigger. This square-shaped signal feeds an RC circuit with a time 
constant tuned so that it is small with respect to the incoming signal period. The output of the RC circuit 
feeds a Schmitt trigger which converts the exponentially decaying signal to a square wave, delayed by the 
time needed to reach the threshold voltage. Having two square waves, one resulting from the original sine-wave 
and the second with a RC-delayed copy of this signal, we generate the pulses driving the LED as an AND 
function between both pulses.
\end{figwindow}

{\bf
\begin{enumerate}
\setcounter{enumi}{3}
\item Considering the period of the signal driving the tuning fork, what is the RC time constant needed 
for the stroboscopic signal?
\item the sound card signal is centered on 0~V (AC signal) while the Schmitt trigger requires a signal 
below a few 100~mV to remain to 0 and otherwise raises its output to the supply voltage. The AC-coupled 
sound card output is DC-offset using a resistor bridge. To prevent DC-leakage to the sound card output 
amplifier, a capacitor is introduced. What is the impedance of a capacitor as a function of frequency? 
select the appropriate capacitor value as a function of the polarizing resistor bridge. What are the 
conditions for a voltage divider resistor bridge to operate properly?
\item Select appropriate component references to assemble the circuit: what integrated circuits provide
the necessary functions?
\end{enumerate}
}

Two chips are provided in DIL packages: the 7414 Schmitt trigger and the 7400 AND gate. 

{\bf
\begin{enumerate}
\setcounter{enumi}{6}
\item After reading the datasheet of these chips, what is a wiring schematic suitable for implementing the
pulse generator driving the LED?
\item Simulate the circuit using {\tt ngspice}. The inverting NAND gate can be simulated using the {\tt hyst} function:
\begin{verbatim}
.model schmitt hyst(in_low=1.49 in_high=3.51 hyst=0 out_lower_limit=5.0 out_upper_limit=0.0 
+ input_domain=0.01 fraction=TRUE)
\end{verbatim}
called in the circuit model with
\begin{verbatim}
a1 1 2 schmitt
\end{verbatim}
\end{enumerate}
}
The result of the SPICE simulation should look like Fig. \ref{spice}.

\begin{figure}[h!tb]
\begin{center}

\end{center}
\caption{Simulation of the stroboscopic generation circuit using {\tt ngspice}. The bold line is the signal at the
output of the pulse shaping circuit driving the LED under control of the purple input sine wave.}
\label{spice}
\end{figure}

\section{Observing the prong motion}

Once the electronic boards have been setup on a breadboard, the tuning fork is located between the LED
and the webcam used to collect pictures of the tuning fork.

\noindent\fbox{\parbox{\linewidth}{The tuning fork prongs are extremely fragile: they are made of
300~$\mu$m thick quartz~! handle with care, and make sure the prongs never hit a wire or the LED when inserting
on the breadboard.}}

\begin{figure}[h!tb]
\begin{center}


\end{center}
\caption{Experimental setup for observing the tuning fork prong oscillation: one sound card output 
drives the tuning fork, while the other output offset by 1~Hz drives the LED stroboscopic signal.}
\label{3}
\end{figure}

\noindent\fbox{\parbox{\linewidth}{In case the sound card is unable to generate 32760~Hz, either because
sampling at 48~kHz or because of a low pass filter when sampling at higher frequency, or if a stronger
driving amplitude is desirable, we might insert a Schmitt trigger before the tuning fork and drive with
a 5-V square wave rather than the direct sound card output. The stronger signal can also drive the tuning
fork using the third harmonic, hence setting GNU Radio audio out frequency to one-third of the tuning fork
resonance frequency. Achieving such a result requires duplicating the bias T circuit on another Schmitt trigger
of the same chip:

\begin{center}

\end{center}
}}
\vspace{0.2cm}

Collecting the movie from the webcam is most easily achieved using VLC or {\tt xawtv} -- the former seems to sometimes exhibit excessively slow framerates and the latter seems
better suited to high-resolution webcams. 

Using the former software, the menu {\tt Media} $\rightarrow$ {\tt Open Capture Device} 
allows for selecting the {\tt Video Device Name}. Select {\tt /dev/video0}. After a few 
seconds, the webcam output should be visible on VLC. Switch off the white LED surrounding 
the lens if needed, and adjust the focus of the lens on the tuning fork. Once the tuning 
fork is well visible, sweep the frequency until the motion of the tuning fork is observed 
on the movie.

When using {\tt xawtv} to view the output of the camera, recording the image stream
is achieved using a different software, namely {\tt ffmpeg}: kill {\tt xawtv} and
record the movie of the vibrating tuning fork with {\tt ffmpeg -f video4linux2 -i /dev/video0 movie.avi}. Alternatively to {\tt xawtv}, FFMPEG also provides a viewer as {\tt
ffplay -i /dev/video0}.

{\bf
\begin{enumerate}
\setcounter{enumi}{7}
\item Considering the tuning fork quality factor, we have already addressed the frequency step needed to
observe the resonance. How quickly can the frequency vary, considering the settling time of the vibration, when
searching for the resonance frequency by sweeping the sound card output frequency?
\end{enumerate}
}

The set of software needed to run the experiment is shown in Fig. \ref{scrt}: sound level is tuned using
{\tt alsamixer}, sound generation at 192~kS/s is driven by GNURadio and its graphical user interface
{\tt gnuradio-companion}, and image capture is achieved using VLC or ffplay. Once the oscillation is observed, 
a movie is recorded using {\tt Playback} $\rightarrow$ {\tt Record} or ffmpeg. We only need a few seconds worth
of movie, so quickly stop the record to keep the file size reasonable.

\begin{figure}
\begin{center}

\end{center}
\vspace{-0.4cm}
\caption{All the tools needed to drive the circuit and acquire the data: top-left is 
the GNURadio flowchart defining the soundcard output signals, top-right is the slider for defining 
the driving signal frequency, bottom-right is the video acquisition software displaying the webcam output
(VLC) and bottom-left is the driving voltage level tuner -- {\tt alsamixer}. The movie version of this
screenshot is at \url{jmfriedt.free.fr/recordmydesktop_tp_tuningfork.ogv}.}
\label{scrt}
\end{figure}

\section{Image processing}

\begin{figwindow}[0,r,,{Tuning fork displacement, in pixel, along the prong length. The prong is clamped at its
upper position which does not move, and the fundamental mode exhibits maximum vibration at the opposite
end of the prong.}\label{fig6}]
Quantitative analysis of the prong motion is addressed using digital image processing. The movie
is converted to a set of individual pictures using for example {\tt mplayer -vo jpeg movie.avi}. Alternatively,
{\tt ffmpeg} can also complete the task, as discussed in the man page. A suitable framework for
image processing is GNU/Octave with its Image Processing toolbox: a color image is read with
{\tt x=imread('imagename.jpg');} 
and converted to a greyscale image by keeping
only the red component: {\tt x=x(:,:,1);}. The prong can be rotated parallel to one of the image axis
by using {\tt imrotate()}.
\end{figwindow}\vspace{0.1cm}

{\bf
\begin{enumerate}
\setcounter{enumi}{8}
\item Motion is detected by searching for matching patterns in \\a ``small'' region of interest between successive images. \\
What signal processing function is used to detect \\similar patterns between two signals?
\item Apply this mathematical function to one line or \\
column of the picture displaying the end of the prong: \\
display the curve of the prong motion over time. The \\
result should look like on of the curves of 
Fig. \ref{fig6}.
\item Repeat the measurement for various frequencies around the resonance, and display the motion
amplitude as a function of frequency.
\end{enumerate}
}
%\vspace{-0.7cm}

\begin{thebibliography}{9}
\bibitem{slom} T. Hunkin \& R. Garrod, {\em Secret Life Of Machines:
The Quartz Watch} (1991), at \url{https://www.youtube.com/watch?v=nQ9_bOIj49s}
\bibitem{jm0} J.-M Friedt, \'E. Carry, {\em Introduction au diapason \`a quartz}, Bull. de l'Union des Physiciens {\bf 879} 1137--1146 (2005) [in French]
\bibitem{jm1} J.-M Friedt, \'E. Carry, {\em Introduction to the quartz tuning fork}, American Journal of 
Physics, pp.415-422 (2007)
\bibitem{jm2} J.Marc, C. Canard, A. Vailly, V. Pichery, J.-M. Friedt, {\em Le diapason \`a quartz comme 
capteur~: utilisation de la carte son de PC pour l'instrumentation}, Bull. de l'Union des Physiciens {\bf 958}, pp.1051--1073 (2013) [in French]
\bibitem{jm3} J.-M. Friedt, {\em Mesure stroboscopique du champ de d\'eplacement d'un diapason \`a quartz 
au moyen d'une carte son et d'une webcam}, Bull. de l'Union des Physiciens {\bf 999} (2017) [in French]
\end{thebibliography}
\end{document}

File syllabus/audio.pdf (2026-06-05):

frequency: f; Options Id: top_block Output Language: Python Generate Options: QT GUI; QT GUI Range Id: f Default Value: 32.768k Start: 32.6k Stop: 32.9k Step: 100m; Variable Id: samp_rate Value: 192k; freq; out; Signal Source Id: analog_sig_source_x_0 Sample Rate: 192k Waveform: Cosine Frequency: 32.768k Amplitude: 1 Offset: 0 Initial Phase (Radians): 0; Signal Source Id: analog_sig_source_x_0_0 Sample Rate: 192k Waveform: Cosine Frequency: 32.769k Amplitude: 1 Offset: 0 Initial Phase (Radians): 0; Audio Sink Id: audio_sink_0 Sample Rate: 192k Device Name: hw:0

frequency: f+df

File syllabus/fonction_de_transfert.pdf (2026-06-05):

displacement (pixel); frame number (a.u.)

0.2

0.3

0.4

0.5

32730 | 32735 | 32740 | 32745 | 32750

displacement amplitude (pixel)

frequency (Hz)

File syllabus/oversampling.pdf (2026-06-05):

raw displacement (pixel); frame number (a.u.)
oversampled displacement (pixel); frame number (a.u.)


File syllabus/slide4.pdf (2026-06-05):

load; synthesizer; tuning fork

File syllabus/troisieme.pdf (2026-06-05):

## audio out

## Vcc

@ f(tuning fork)/3 | ∼50Ω

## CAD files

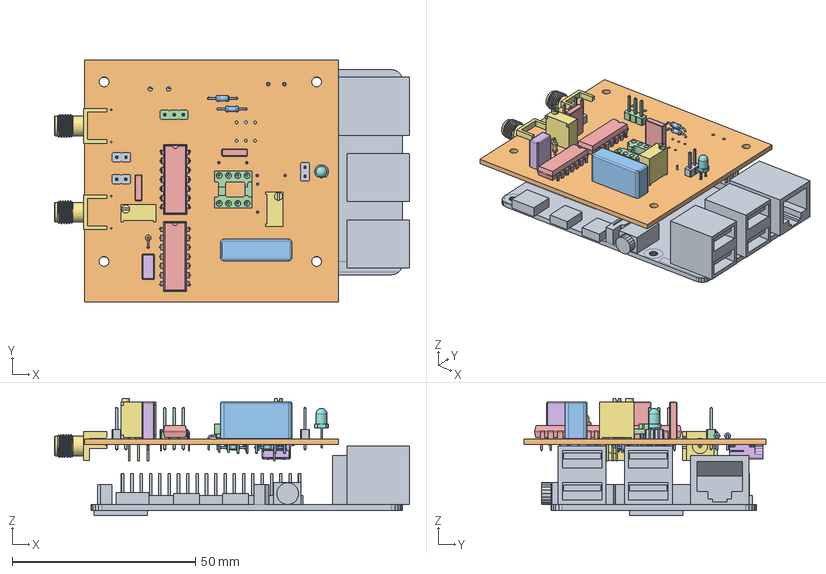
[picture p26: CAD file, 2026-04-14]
kicad/assemblage.FCStd
96.9 x 66.0 x 32.1 mm
Raspberry Pi 4 B
Pcb_b420
U4_Converter_DCDC_muRata_NMAxxxxSC_THT_15c1a6471cf0
J1_PinHeader_1x03_P254mm_Vertical_bea3a77023fa
U1_DIP-14_W7.62mm_b974a9d0bc6e x 2
C1_C_Rect_L70mm_W35mm_P500mm_3575e4c21ad4
RV2_Potentiometer_Bourns_3296W_Vertical_47eb96743217 x 2
D1_LED_D3.0mm_06b240ffe131
J2_PinHeader_1x02_P254mm_Vertical_4e86ba224d96 x 3
R1_R_Axial_DIN0204_L36mm_D16mm_P254mm_Vertical_ecaf4bfbc7cb
R7_R_Axial_DIN0204_L36mm_D16mm_P762mm_Horizontal_7e64e2e1e501 x 5
U3_DIP_8_W762mm_Socket_205615dfe45d
C5_C_Rect_L70mm_W20mm_P500mm_10e1155419b8 x 2
J4_USB_Mini-B_Lumberg_2486_01_Horizontal_ad8e519da88b
J6_SMA_Molex_73251-1153_EdgeMount_Horizontal_1c6464897526 x 2
C2_C_0805_2012Metric_26ee54c06e16 x 2

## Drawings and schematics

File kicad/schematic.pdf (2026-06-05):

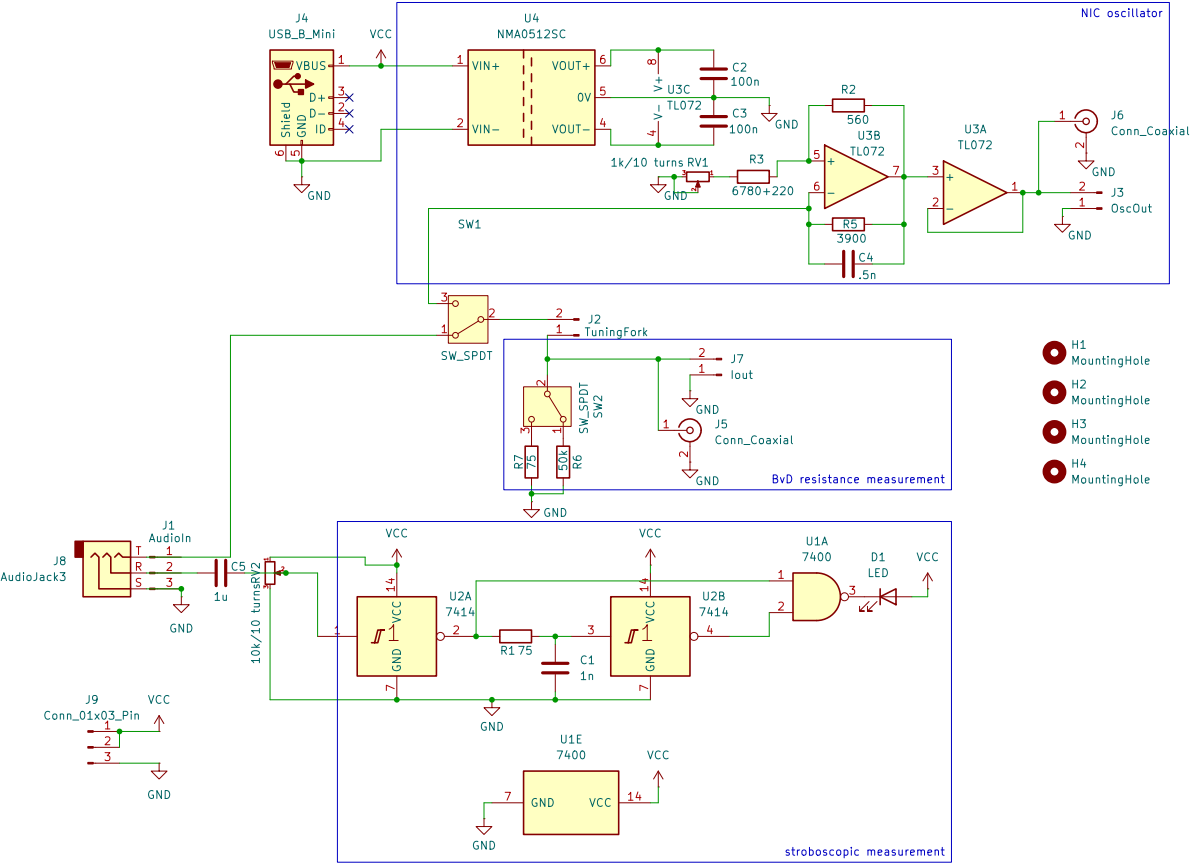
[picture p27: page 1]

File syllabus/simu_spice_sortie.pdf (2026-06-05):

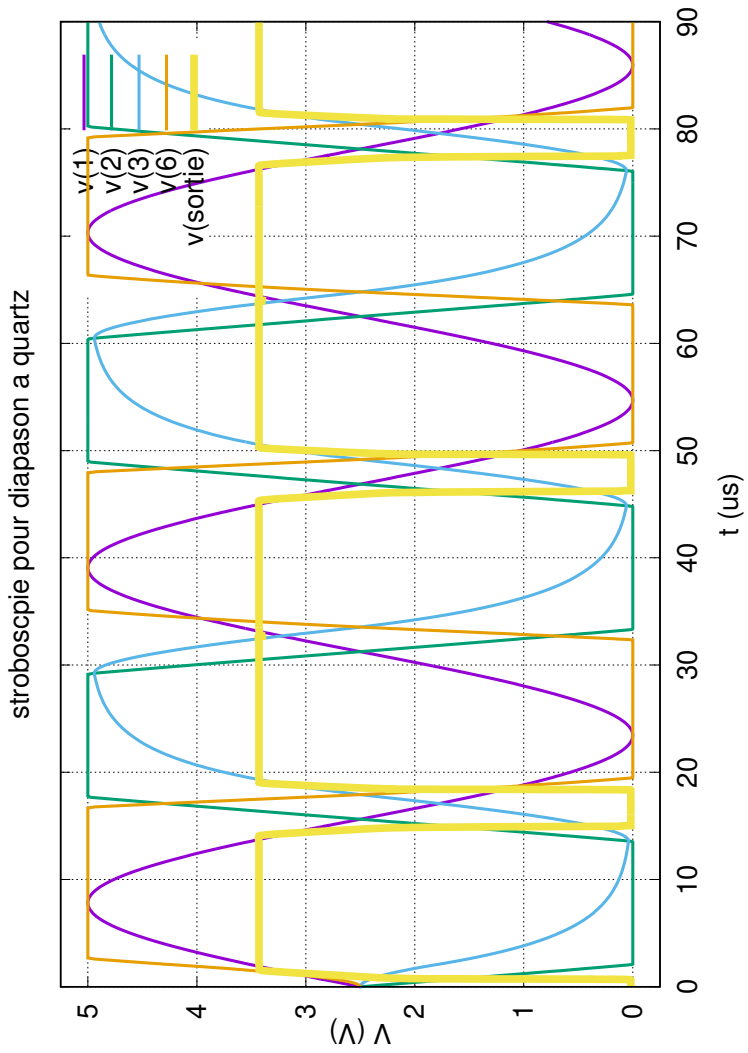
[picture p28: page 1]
v(sortie)

stroboscpie pour diapason a quartz

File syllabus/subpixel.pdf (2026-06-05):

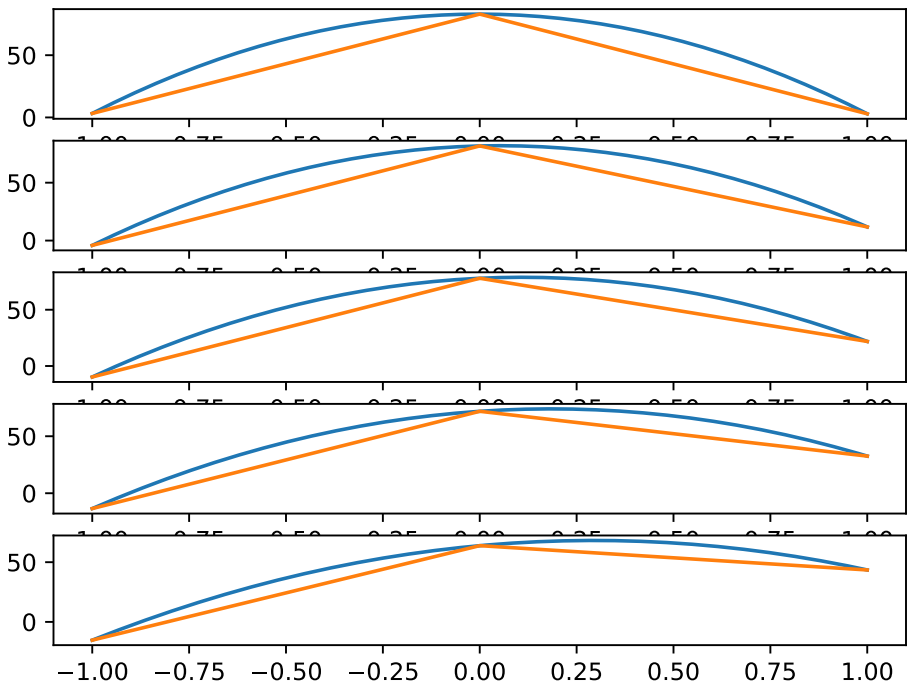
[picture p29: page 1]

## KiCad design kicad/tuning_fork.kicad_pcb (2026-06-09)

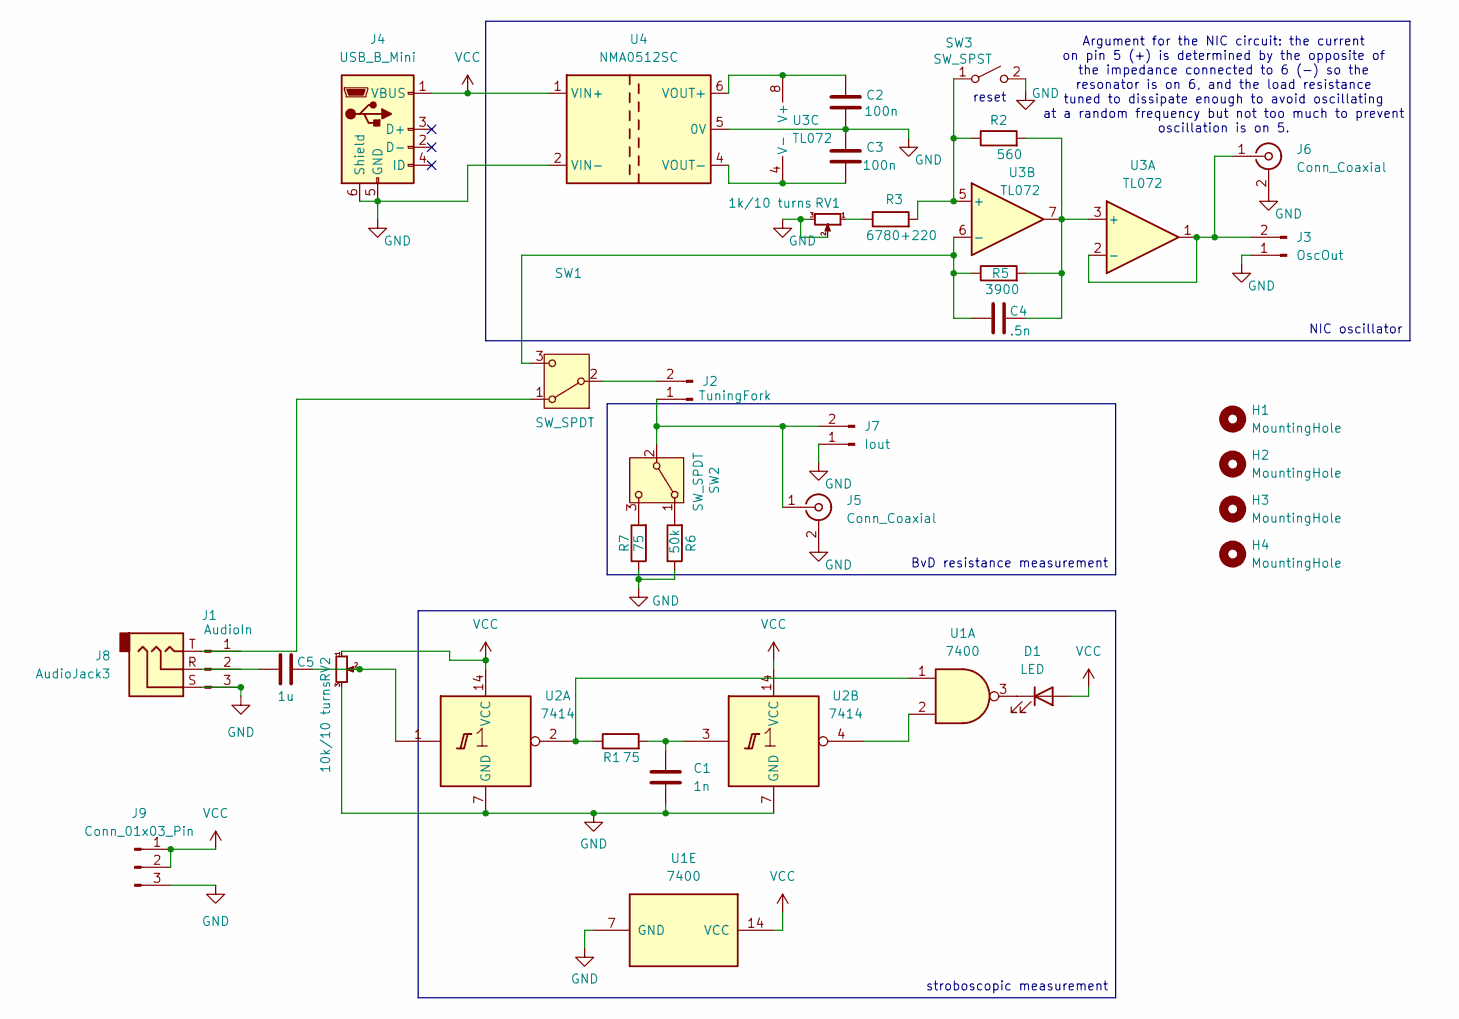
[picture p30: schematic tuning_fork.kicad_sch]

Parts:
C1: 1n; C_Rect_L7.0mm_W3.5mm_P5.00mm
C2, C3: 100n; C_0805_2012Metric_Pad1.18x1.45mm_HandSolder
C4: .5n; C_Rect_L7.0mm_W2.0mm_P5.00mm
C5: 1u; C_Rect_L7.0mm_W2.0mm_P5.00mm
D1: LED; LED_D3.0mm
H1, H2, H3, H4: MountingHole; MountingHole_3.2mm_M3
J1: AudioIn; PinHeader_1x03_P2.54mm_Vertical
J2: TuningFork; PinHeader_1x02_P2.54mm_Vertical
J3: OscOut; PinHeader_1x02_P2.54mm_Vertical
J4: USB_B_Mini; USB_Mini-B_Lumberg_2486_01_Horizontal
J5, J6: Conn_Coaxial; SMA_Molex_73251-1153_EdgeMount_Horizontal
J7: Iout; PinHeader_1x02_P2.54mm_Vertical
J8: AudioJack3; Jack_3.5mm_Lumberg_1503_02_Horizontal
J9: Conn_01x03_Pin; PinSocket_1x03_P2.54mm_Vertical
R1: 75; R_Axial_DIN0204_L3.6mm_D1.6mm_P2.54mm_Vertical
R2: 560; R_Axial_DIN0204_L3.6mm_D1.6mm_P7.62mm_Horizontal
R3: 6780+220; R_Axial_DIN0204_L3.6mm_D1.6mm_P7.62mm_Horizontal
R5: 3900; R_Axial_DIN0204_L3.6mm_D1.6mm_P7.62mm_Horizontal
R6: 50k; R_Axial_DIN0204_L3.6mm_D1.6mm_P7.62mm_Horizontal
R7: 75; R_Axial_DIN0204_L3.6mm_D1.6mm_P7.62mm_Horizontal
RV1: 1k/10 turns; Potentiometer_Bourns_3296W_Vertical
RV2: 10k/10 turns; Potentiometer_Bourns_3296W_Vertical
SW1, SW2: SW_SPDT; SW_Slide-03_Wuerth-WS-SLTV_10x2.5x6.4_P2.54mm
SW3: SW_SPST; SW_TH_Tactile_Omron_B3F-100x
U1: 7400; DIP-14_W7.62mm
U2: 7414; DIP-14_W7.62mm
U3: TL072; DIP-8_W7.62mm_Socket
U4: NMA0512SC; Converter_DCDC_Murata_NMAxxxxSC_THT

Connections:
GND: C1.2, C2.2, C3.1, J1.3 (Pin_3_3), J3.1, J4.5 (GND), J4.6 (Shield), J5.2 (Ext), J6.2 (Ext), J7.1, J8.S, J9.3, R6.1, R7.1, RV1.2, RV1.3, RV2.3, SW3.2 (B), U1.7 (GND), U2.7 (GND), U4.2 (VIN-), U4.5 (0V)
unnamed: C1.1, R1.2, U2.3
unnamed: C5.1, J8.R
unnamed: C5.2, RV2.2, U2.1
unnamed: D1.1 (K), U1.3
unnamed: J2.1, J5.1 (In), J7.2, SW2.2 (B)
unnamed: J2.2, SW1.2 (B)
unnamed: J3.2, J6.1 (In), U3.1, U3.2 (-)
unnamed: R1.1, U1.1, U2.2
unnamed: R3.1, RV1.1
unnamed: J8.T, SW1.1 (A)
unnamed: C4.1, R5.1, SW1.3 (C), U3.6 (-)
unnamed: R6.2, SW2.1 (A)
unnamed: R7.2, SW2.3 (C)
unnamed: R2.1, R3.2, SW3.1 (A), U3.5 (+)
unnamed: U1.2, U2.4
unnamed: C4.2, R2.2, R5.2, U3.3 (+), U3.7
unnamed: C2.1, U3.8 (V+), U4.6 (VOUT+)
unnamed: C3.2, U3.4 (V-), U4.4 (VOUT-)
VCC: D1.2 (A), J4.1 (VBUS), J9.1, J9.2, RV2.1, U1.14 (VCC), U2.14 (VCC), U4.1 (VIN+)

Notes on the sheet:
reset
Argument for the NIC circuit: the current on pin 5 (+) is determined by the opposite of the impedance connected to 6 (-) so the resonator is on 6, and the load resistance tuned to dissipate enough to avoid oscillating at a random frequency but not too much to prevent oscillation is on 5.
stroboscopic measurement
BvD resistance measurement
NIC oscillator

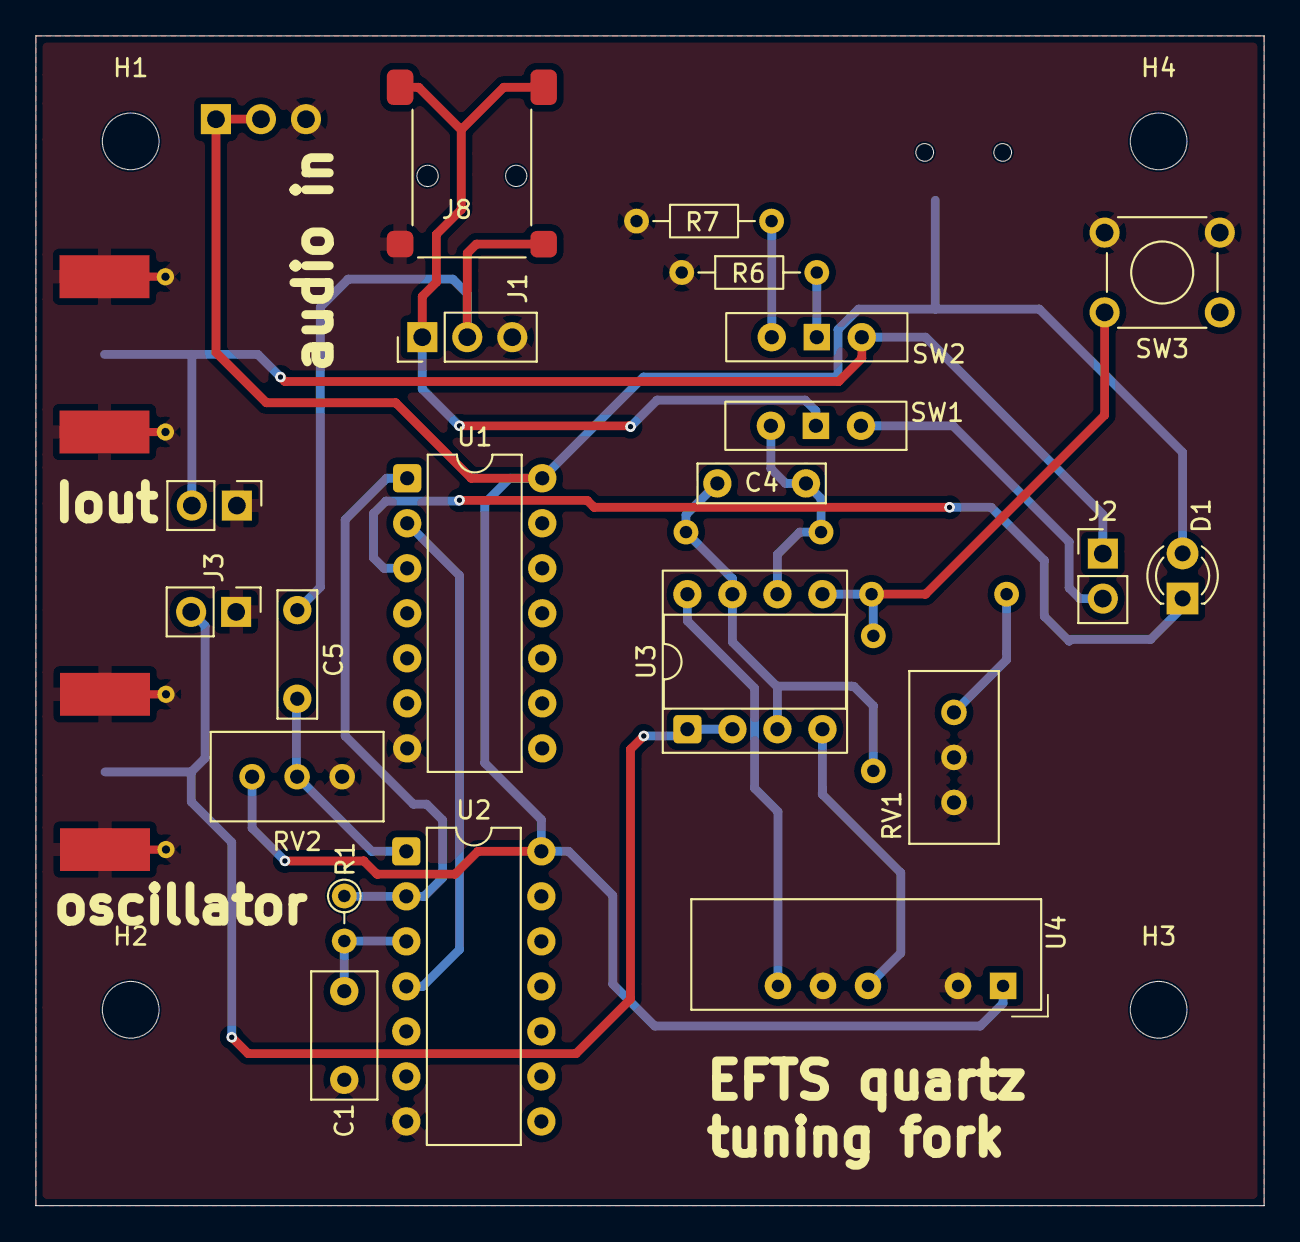
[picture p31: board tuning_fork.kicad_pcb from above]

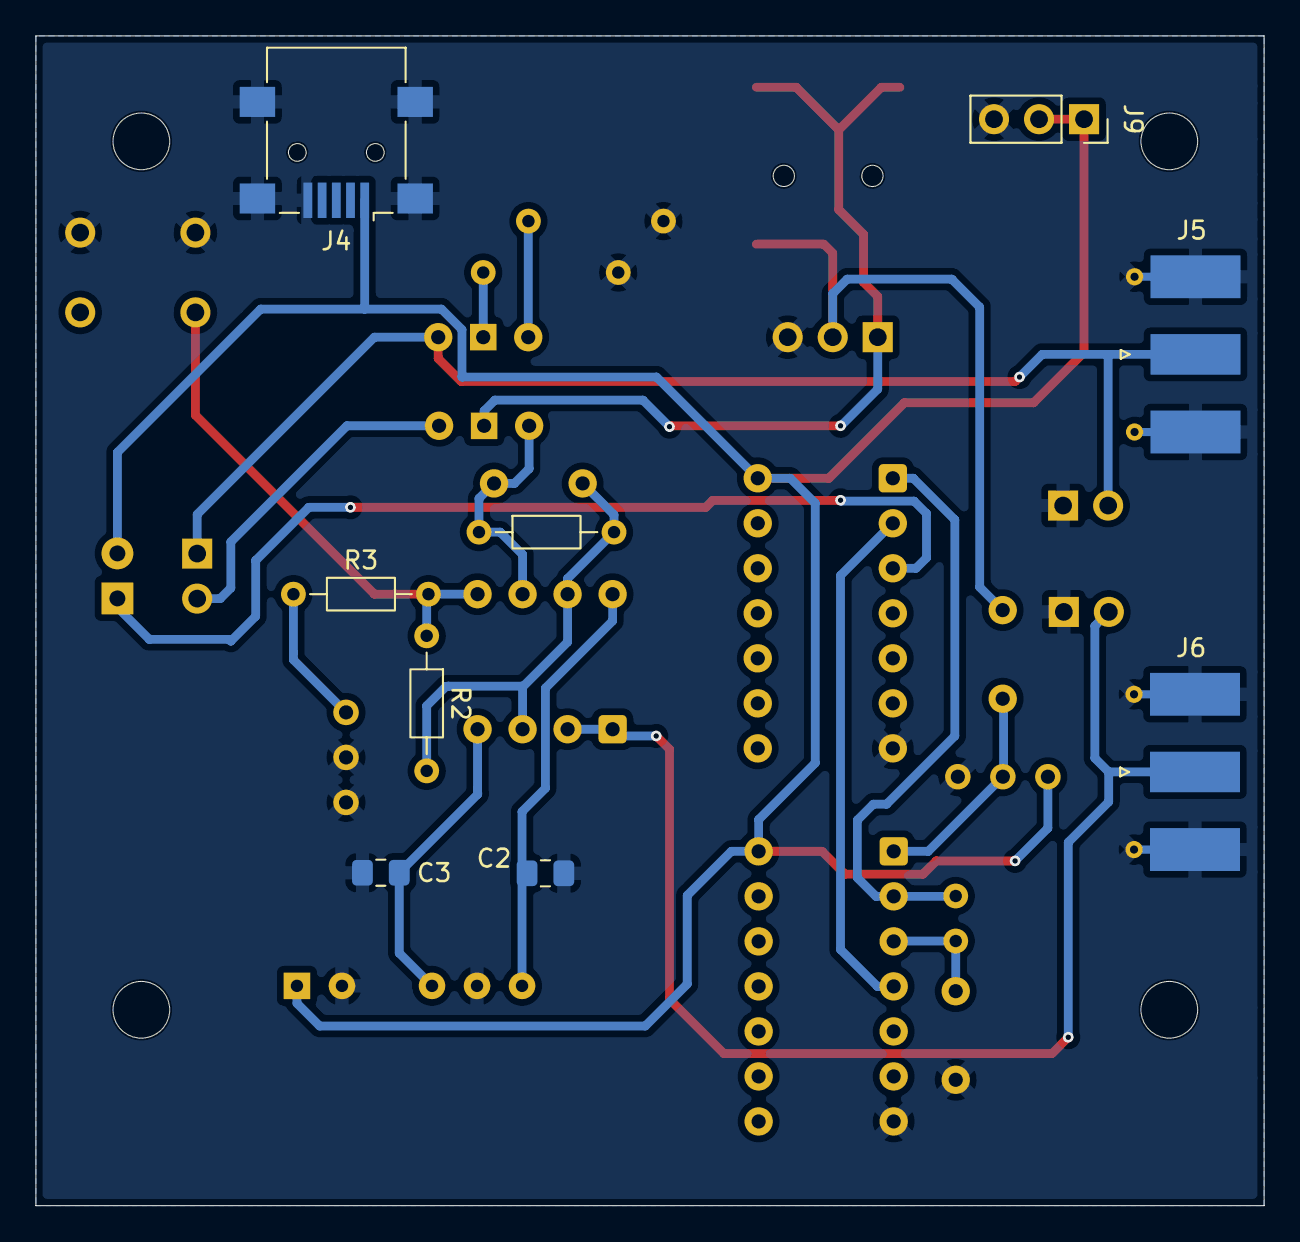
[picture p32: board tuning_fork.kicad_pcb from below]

Board: 2 copper layers, 69.3 x 66.0 mm, 34 parts (9 on the bottom side), 20 nets.

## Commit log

2026-04-10 move mounthing holes to RPi5 location
    [tuning_fork.kicad_pcb]
2026-04-14 improved layout for usability
    [assemblage.FCStd, tuning_fork.kicad_pcb]
2026-05-21 add RPi +5V supply header
    [tuning_fork.kicad_pcb, tuning_fork.kicad_sch]
2026-06-09 add oscillator reset push button
    [tuning_fork.kicad_pcb, tuning_fork.kicad_sch]
2026-06-10 add impedance analyzer measurement
    [TRACE02-25-02-2026-AVG32.CSV]
